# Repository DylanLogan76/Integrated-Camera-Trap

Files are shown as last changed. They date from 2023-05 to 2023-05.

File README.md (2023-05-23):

Integrated-Camera-Trap

Advisors: <br />
Professor Duncan Irschick: (https://www.bio.umass.edu/biology/about/directories/faculty/duncan-j-irschick) <br />
Professor David Schmidt: (https://mie.umass.edu/faculty/david-schmidt) <br />
Professor Marco Duarte (ECE SDP Advisor) : (https://ece.umass.edu/faculty/marco-duarte) <br />

Network of Raspberry Pis connected with Camera Modules to take synchronized pictures via WIFI using Message Query Telemetry Transport (MQTT) (Mosquitto) triggered by motion sensors

If you need access to this repository, contact me at my email address: dylanlogan76@gmail.com and cc Professor Duncan 
Irschick and/or Professor David Schmidt and ask them to grant permission. Please provide your github username as well.

Past work by:
Senior Design Project 2020 Team 15

Members: <br />
Anamitra Datta  <br />
Max Haimowitz <br />
Xiaoyang Pan <br />
Minting Chen <br />

Indepedant Study: Zalman Lipschitz
                  Dylan Logan

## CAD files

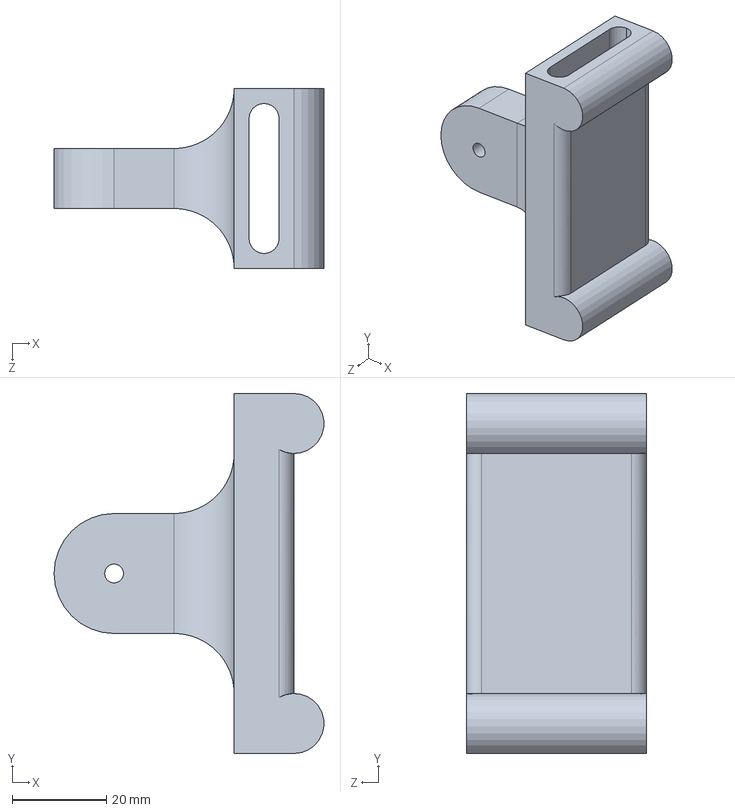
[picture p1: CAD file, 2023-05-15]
Enclosure_Files/Mount.SLDPRT
57.1 x 76.2 x 38.1 mm

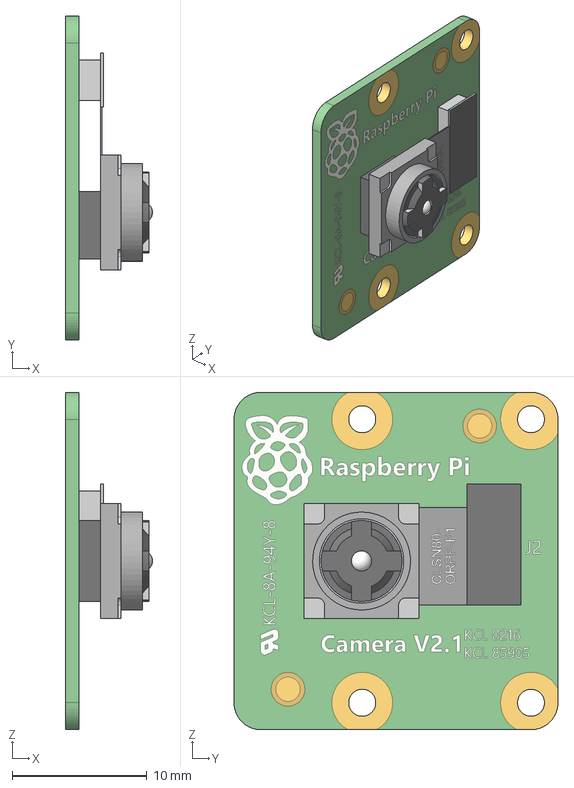
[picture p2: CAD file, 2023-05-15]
Enclosure_Files/Cam V2.1 v1.step
6.45 x 24.0 x 25.0 mm

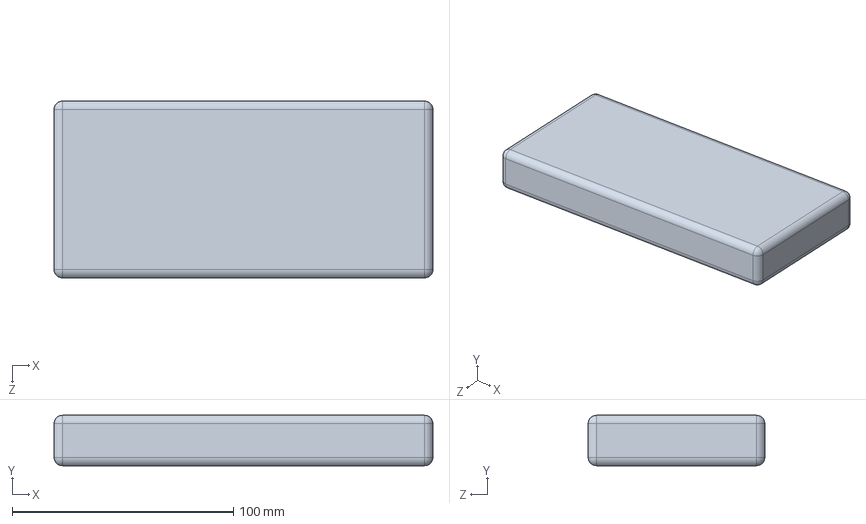
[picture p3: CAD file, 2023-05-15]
Enclosure_Files/Battery Mockup.SLDPRT
171.4 x 22.9 x 80.0 mm

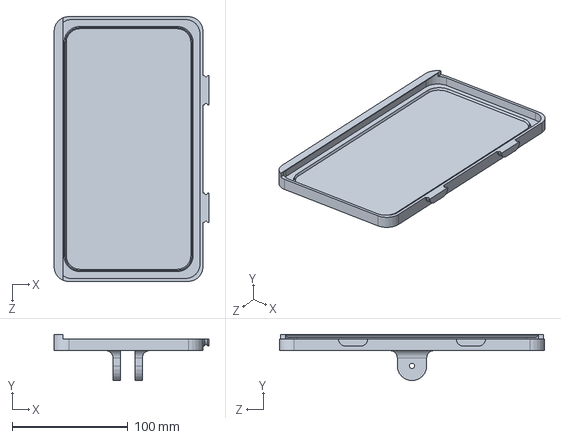
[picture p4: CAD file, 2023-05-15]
Enclosure_Files/Lid.SLDPRT
133.6 x 39.9 x 228.6 mm

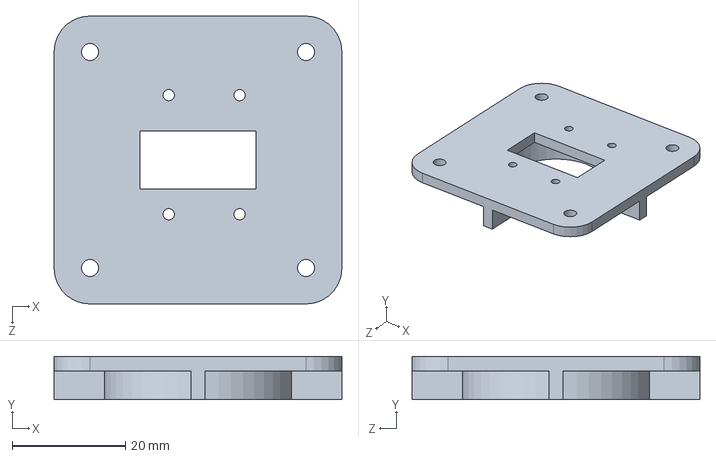
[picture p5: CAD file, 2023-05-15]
Enclosure_Files/Camera Bracket.SLDPRT
50.8 x 7.62 x 50.8 mm

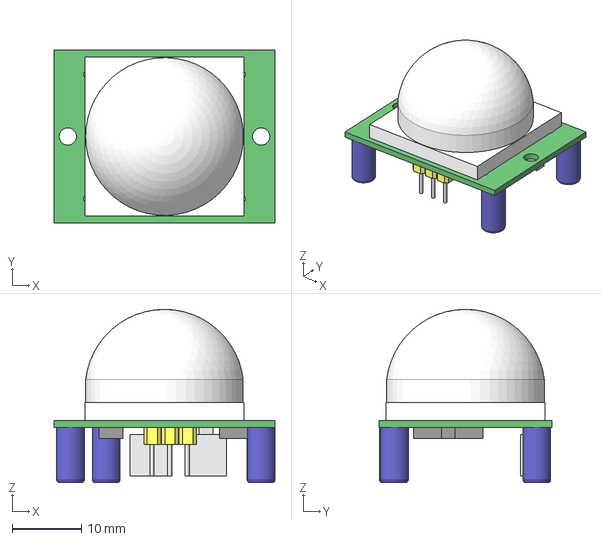
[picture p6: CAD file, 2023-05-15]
Enclosure_Files/HCSR501.step
32.0 x 25.0 x 25.1 mm

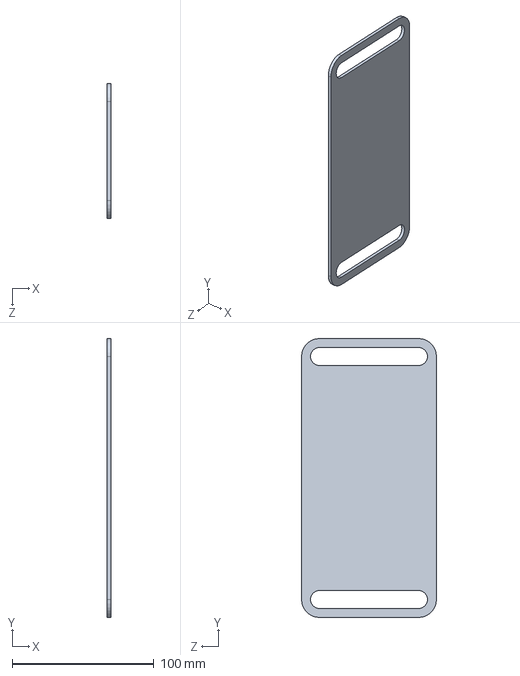
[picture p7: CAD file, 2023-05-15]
Enclosure_Files/Separator.SLDPRT
2.54 x 196.9 x 95.2 mm

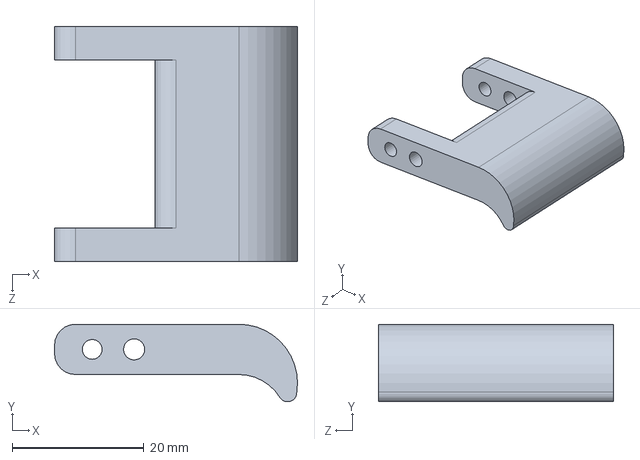
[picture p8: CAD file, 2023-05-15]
Enclosure_Files/Latch.SLDPRT
36.8 x 11.7 x 35.6 mm

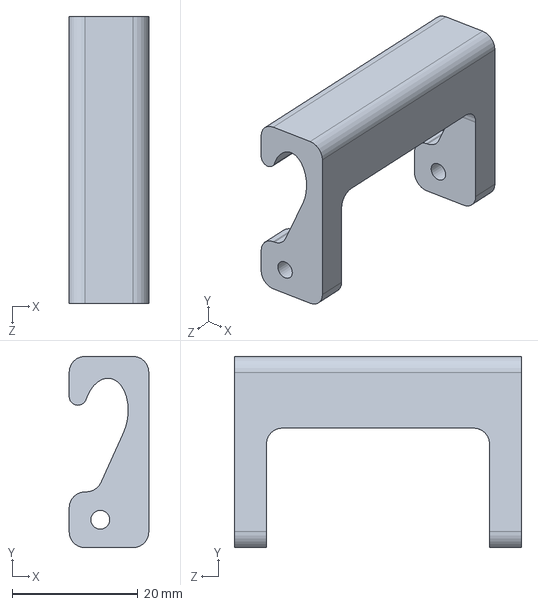
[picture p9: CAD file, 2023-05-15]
Enclosure_Files/Hook.SLDPRT
12.7 x 30.5 x 45.7 mm

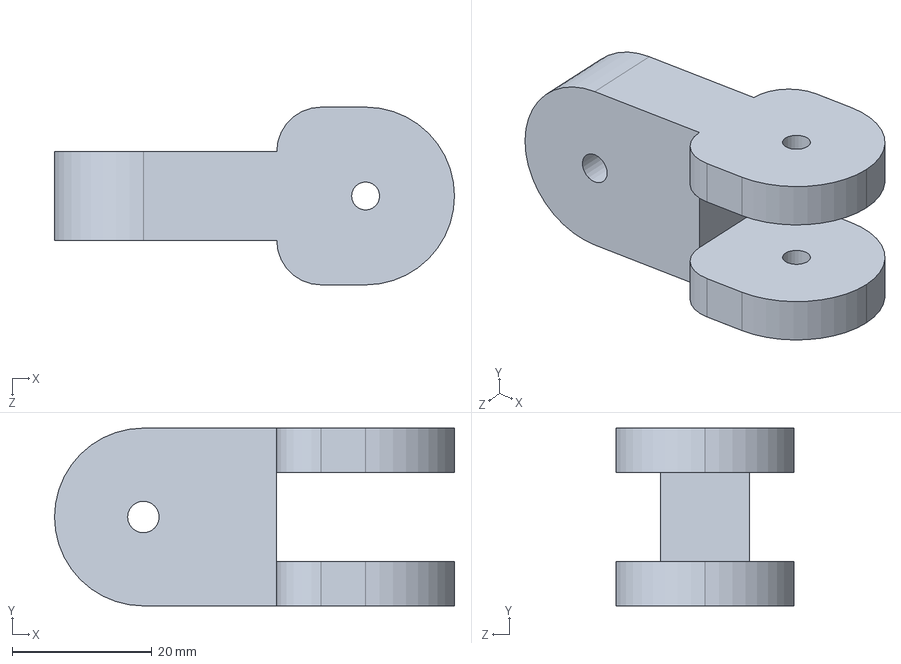
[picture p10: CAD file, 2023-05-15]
Enclosure_Files/Swivel.SLDPRT
57.2 x 25.4 x 25.4 mm

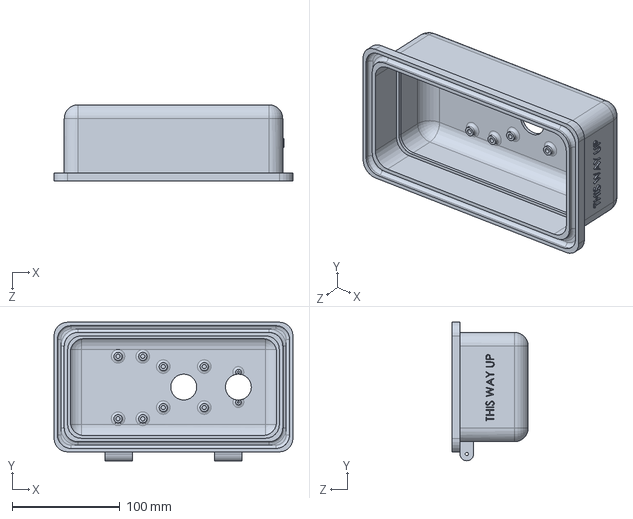
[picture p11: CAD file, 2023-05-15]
Enclosure_Files/Case.SLDPRT
222.2 x 128.9 x 71.1 mm

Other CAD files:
Enclosure_Files/Hook_Legacy.SLDPRT

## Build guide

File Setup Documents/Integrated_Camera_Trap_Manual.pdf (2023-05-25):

# Integrated Camera Trap

## Installation Guide and Instruction Manual

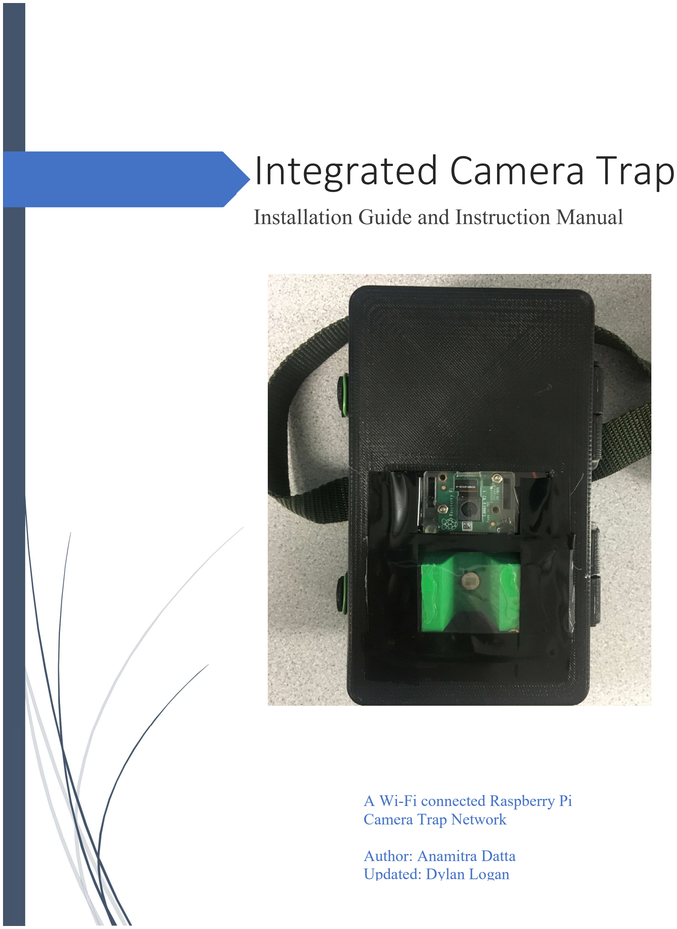
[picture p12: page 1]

A Wi-Fi connected Raspberry Pi Camera Trap Network

Author: Anamitra Datta
Updated: Dylan Logan

1

## Contents

2

3

## 1. Introduction

### a. Background

Camera Traps have been used by biologists and wildlife researchers to observe animals through the use of photos and 3D modeling rather than dangerous and disruptive physical techniques such as tranquilization and traps which can disturb and harm animals. However, the problem with current camera traps is that they are neither connected nor synchronized. This becomes an issue when photo sets generated by the camera traps are used for 3D modeling, resulting in poor, disconnected, and fragmented models as a result of desynchronized photos. Our system aims to improve this issue by connecting the camera traps through Wi-Fi and ensuring photo capturing synchronization through timed messages sent over Wi-Fi, telling each camera trap when to take a photo.

### b. Network Design

Our network uses a master-slave paradigm in which one “master”/main device sends messages to all the of the “slave”/secondary devices when to take a photo. The figure below shows how to the system is set up.

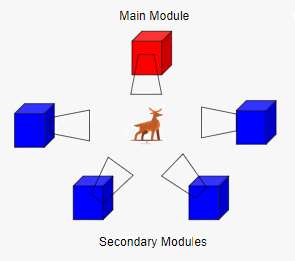
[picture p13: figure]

The camera traps should be arranged in a circle around a single point/area of focus where an animal is likely to appear. There should only be one “master” device in the network and the rest of the devices should be “slave” devices.

4

### c. Hardware

Our camera trap runs on a Raspberry Pi Zero WH (Wireless with Headers) as shown below

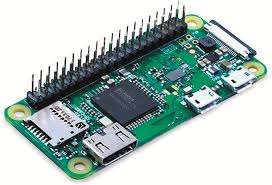
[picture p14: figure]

A Raspberry Pi is a small single-board computer. This board functions like a normal computer in which you can run software and even install physical components.
More information about the Raspberry Pi can be found on the official Raspberry Pi website: https://www.raspberrypi.org/

### d. Software and Networking

The system runs on Wi-Fi through the use of either a router or a wireless access point that can be set up using a Raspberry Pi.
The messages sent within the system are through the use of MQTT (Message Queuing Telemetry Transport). A “broker” is used to send or “publish” messages to all devices listening or “subscribing” to an MQTT “topic” or channel within a network. The broker/publisher and subscribers can be set up using Mosquitto, a free, open-source software for MQTT. More information about Mosquitto can be found on the official Mosquitto website: https://mosquitto.org/
The code running the camera synchronization and photo capturing script is written in Python. More information about Python can be found on the official Python website: https://www.python.org/

5

## 2. Unix

### a. Introduction to Unix

The Raspbian OS that the Raspberry Pi uses is part of the Linux/Unix OS family. Knowledge of this OS and how to use it is necessary for this system. This chapter covers all of the basic topics of the Raspbian OS that are needed for this system to function.

### b. Basic commands

The main way people use a Linux/Unix based operating system is through the command line or terminal. In this section we will cover some basic command line functions so you can get used to working in a Linux/Unix environment. Documentation for Linux commands: http://man7.org/linux/man-pages/index.html . Also type “man <command name>” to get information about a particular Linux command.
i. ls
This lists the contents of the directory you are currently in or the directory you specify
ii. cd
This changes the directory you are currently in. If you want to change to a different directory type this command.
iii. mv
Move a file to a destination directory optionally with a different name and delete the old file. iv. cp
Copy a file to a destination directory optionally with a different name and preserve the old file.
v. rm
Remove a file or directory
vi. mkdir
Make a directory
vii. pwd
Print the current working directory you are in.

6

Permissions
Permissions control who can read, write, or execute a file or directory. Root has the highest permission in Unix subsystems. To be a root user, you must in the sudoers list in the operating system (you are automatically in it by default on Raspbian). Next you must type in the command “sudo su” to change to the root user. Sometimes you need a password to become the root user. If you ever need root privilege to execute a command type “sudo” before your whole command. viii. chmod
Change read, write, and execute permissions of a file.
ix. chown
Change who owns a file or directory.

### c. Processes

Programs and other software that run on an Operating System are referred to as processes. When you execute a program or command, it will run as a process. Here are commands that deal with processes:
i. ps
Lets you view all process running on the operating system. Alternatives include top or htop ii. kill
Kill or stop a process from executing

### d. Power

i. reboot
Restart/reboot the Pi
ii. poweroff
Shutdown the Pi.

### e. Startup services

In our system, we have programs that must start up immediately when the Raspberry Pi boots up. There are many different ways to start programs up on boot.

i. rc.local
This is a file that starts just after all normal services have been started. This is just a bash script file which can run shell commands or any software commands. It is located in the /etc/ folder.

For example, we can start the mobile app with the command “python -u ct_mobile_server.py > output.txt 2>error.txt </dev/null &” and put it in the rc.local file. This starts the mobile app

7

server as a background process and writes the output and errors to separate files on startup, as long as it connected to a proper Wi-Fi network.

ii. Systemd
https://www.freedesktop.org/wiki/Software/systemd/https://www.raspberrypi-spy.co.uk/2015/10/how-to-autorun-a-python-script-on-boot-using-systemd/
Systemd is a service manager which can control which process can run on startup and run them as a service file.

To set a python program (for example, the CT slave program) as a systemd service, write the service file with the command “sudo nano /lib/systemd/ctslave.service”
(Note: these can also be saved to the /lib/systemd/services directory)

Add in the following to the ctslave.service file and save it:
[Unit]
Description=Camera Trap Slave Service After=network-online.target Wants=network-online.target

[Service]
Type=idle
User=pi
ExecStart=python -u /home/pi/ct_client_slave.py

[Install]
WantedBy=network-online.target

Give the file root permissions with the command “sudo chmod 777 /lib/systemd/ctslave.service” Type in the commands “sudo systemctl daemon-reload” and “sudo systemctl enable ctslave.service” and then reboot the pi. The program should successfully run on startup. You can check using “sudo systemctl status ctslave.service” . You can check the output of the service using journalctl.

You can start the mobile app server or the slave or master CT programs using systemd

iii. Cron
http://man7.org/linux/man-pages/man5/crontab.5.html
Cron is a software utility which provides a time based job scheduler. You can start scripts or programs at specific times. Here is a guide on how to write a crontab to automatically start a program or command: https://help.ubuntu.com/community/CronHowto

8

## 3. Installation and Setup

### Camera Trap Raspberry Pi a. Supplies

The supplies we used are listed below, but you can use any components that are similar and fit within the enclosure
PIR Motion Sensor | Adafruit | HC-SR501 | $10.00
Raspberry Pi Zero WH | Raspberry Pi | Zero WH | $14.00
Raspberry Pi Camera Module V2 (8 Megapixel,1080p) | Raspberry Pi | V2, 8MP, 1080p | ~$25.00

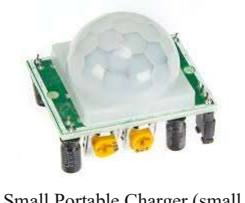
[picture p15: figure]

Portable Charger | Sethruki | 20000mAh, T-28 | ~$25.00
Raspberry Pi Zero WH (Wireless With Headers) | HC-SR501 PIR Motion Sensor

Small Portable Charger (small

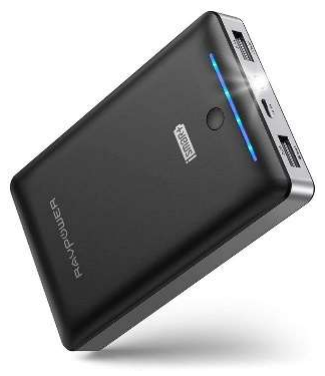
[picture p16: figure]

enough to fit in enclosure)

MicroSD card (16-32 GB) and SD Card Adapter | Micro USB to USB adapter or
| USB Hub (for USB Wireless Mouse and Keyboard)

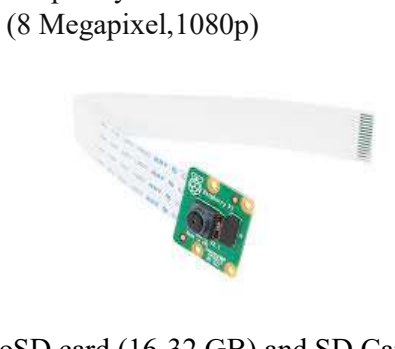
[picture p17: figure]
(8 Megapixel,1080p)

Raspberry Pi Camera Module V2

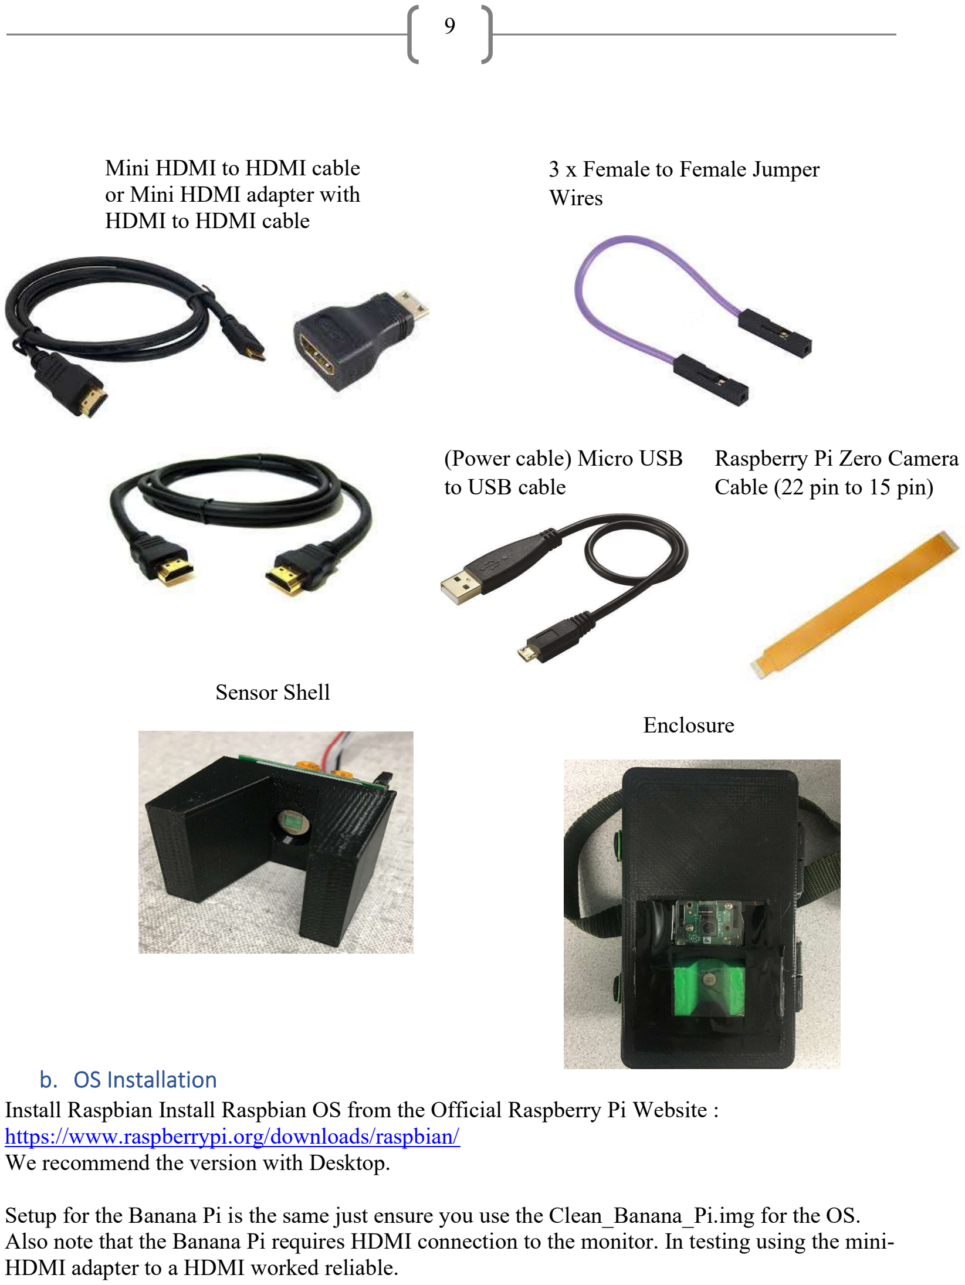
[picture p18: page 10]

9

### b. OS Installation

Install Raspbian Install Raspbian OS from the Official Raspberry Pi Website : https://www.raspberrypi.org/downloads/raspbian/
We recommend the version with Desktop.

Setup for the Banana Pi is the same just ensure you use the Clean_Banana_Pi.img for the OS. Also note that the Banana Pi requires HDMI connection to the monitor. In testing using the mini-HDMI adapter to a HDMI worked reliable.

Mini HDMI to HDMI cable
or Mini HDMI adapter with
HDMI to HDMI cable

### 3 x Female to Female Jumper

Wires

(Power cable) Micro USB
to USB cable

Raspberry Pi Zero Camera
Cable (22 pin to 15 pin)

Sensor Shell
Enclosure

10

Put the microSD card in the SD Card adapter and put the SD card adapter into your SD card slot on your computer.
First, unzip the downloaded folder to get an .img file of the Operating system you want to install on the Pi. To install the Raspbian OS on the microSD card, we recommend to use Etcher : https://www.balena.io/etcher/ . Flash the image or .img file onto the SD card and remove the microSD card from the SC card adapter when the installation is complete.

### c. Setting up the Raspberry Pi

i. Add components and start up OS

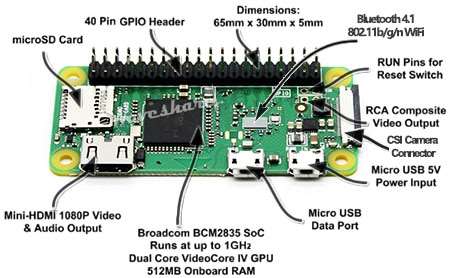
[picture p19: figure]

Place the microSD card into the microSD card slot on the Raspberry Pi

Put the 22 pin side of the wire on the bottom slot of the camera module and the 15 pin side of the wire in the Raspberry Pi CSI camera connector on the end of the Pi. Make sure the dark or white part of the wire faces up. Make sure the camera is attached as shown below.

11

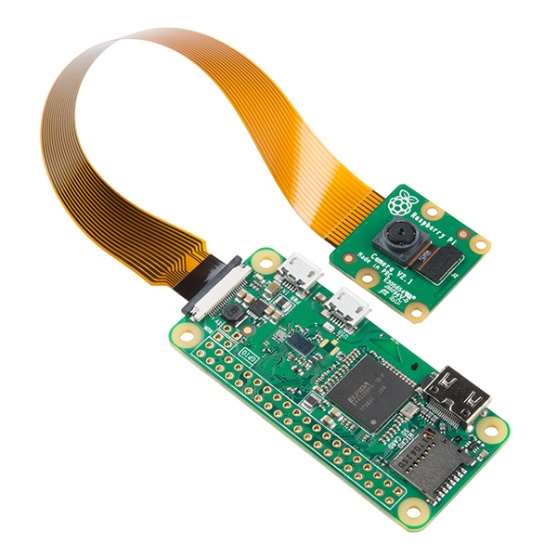
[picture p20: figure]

Attach the PIR Sensor with the female to female jumper wire cables to the Raspberry Pi Zero as shown below. Make sure the pins match with each other.

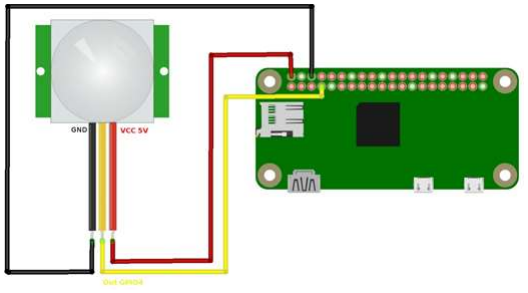
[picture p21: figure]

Plug in the Micro USB to USB adapter/hub in the Micro USB data port and attach your wireless USB Mouse and Keyboard
Plug in the mini HDMI to HDMI cable or mini HDMI adapter to the mini HDMI port and attach an HDMI cable to a computer Desktop monitor
Finally, plug in the power cable to the Pi in the micro USB power input port and attach it to a power outlet or a small portable charger
A few Raspberry Pi logos, a rainbow-colored screen, and maybe some startup scripts should appear. This means that the Raspbian OS is booting up and you had successfully installed the OS on the Pi. If it does not work, make sure you have followed all of the steps, make sure the Pi works properly and make sure the image is installed on the microSD card correctly and make sure the microSD card is working properly.

12

The default username is "pi" and the default password is "raspberry"
The default username is “pi” and the default password is “bananapi”

You can change the password for user "pi" if you want, but it is not necessary. Follow these instructions: https://www.raspberrypi.org/documentation/linux/usage/users.md

If you want to change the password, use the command “passwd” or type in “sudo raspi-config” and select option 1. Change User Password

If you are using a Headless Raspbian OS without a GUI/Desktop, edit XKBLAYOUT line in /etc/default/keyboard from "gb" to "us" using nano with the command “sudo nano /etc/default/keyboard”

ii. Wi-Fi Setup
Follow these instructions to set up Wi-Fi depending on your setup: https://www.raspberrypi.org/documentation/configuration/wireless/ You need to connect to the Internet for the next few steps.
Desktop:
In the upper right corner, there should be network icon that looks like this:
Click it, and click on the Wi-Fi network you want to connect to and type in the password of the Wi-Fi network. When the icon becomes fully blue, you should be fully connected to Wi-Fi Command Line:
Type in “sudo raspi-config” and select 2. Network Options and then 2.Wi-Fi. Type in the ssid of the network you want to connect to and its password. After that, reboot the Pi and you should be connected to the Wi-Fi network you specified.
Or
You can edit the /etc/wpa_supplicant/wpa_supplicant.conf file to add this line at the bottom: network={
| ssid="<name of Wifi Network>" psk="<Password for that Wifi Network>"

}

Then reboot the Pi and should you be able to connect to the Wi-Fi network specified. Depending on your Wi-Fi network configurations, you might need to add extra parameters to connect, see the documentation for more details,
http://w1.fi/cgit/hostap/plain/wpa_supplicant/wpa_supplicant.conf -Documentation for wpa_supplicant.conf

13

To set up a static IP address for the Raspberry Pi, edit the dhcpcd.conf file using the command “sudo nano /etc/dhcpcd.conf” and add the following line with the ip address you want to set the Pi to specifically (24 is the subnet mask)
static ip_address=192.168.5.1/24

iii. Installation software and enabling interfaces
When you are connected to the internet, type in the following in the command line and type "y" when asked to install the following:
sudo apt-get update
sudo apt-get upgrade
sudo apt-get install mosquitto mosquitto-clients sudo apt-get install python-pip
sudo pip install paho-mqtt
sudo apt-get install ftpd
sudo pip install gpiozero
sudo pip install picamera
sudo apt-get install fbi
sudo apt-get install sshpass
sudo apt-get install python-paramiko

SSH (protocol to log into Pi remotely) is disabled by default, we need to enable SSH to enable SSH:

### 1. type "sudo raspi-config" in the command line 2. Select 5.Interfacing Options 3. Select P2 SSH 4. reboot the pi by typing "sudo reboot" in the command line

SSH in now enabled and you can SSH into the Pi from any device using a software client or through command line (https://man.openbsd.org/ssh)

FTP or SCP files from https://github.com/anamitradatta/Integrated-Camera-Trap for each Pi. We recommend an FTP or SCP client:

WinSCP (Windows only)
Filezilla
Cyberduck

The camera is disabled by default, we need to enable Camera

14

to enable camera:

### 1. type "sudo raspi-config" in the command line 2. Select 5.Interfacing Options 3. Select P1 Camera 4. reboot the pi by typing "sudo reboot" in the command line

The Camera is now enabled and working
If you want to test the camera, run test_camera.py to see if it can take a photo "test_photo.jpg"

In the main source code folder, type in the command "sudo chmod 777 ./*" and "sudo chown pi ./*" to run all files as user pi without root permissions

Make a directory called cameraTrapPhotos in the /home/pi directory.

Python should be pre-installed on Raspbian OS. Make sure python or python3 is installed on your OS by typing in "python --version", if returns nothing, then you need to install python for Linux https://www.python.org/downloads/source/

### Access Point Raspberry Pi

In our system, we will be using and setting up a Raspberry Pi Zero W to act as an access point or router in our system so we do not need the use of a physical router or switch in our network.
i. Supplies
Raspberry Pi Zero W or WH | Small Portable Charger (small enough to fit in enclosure)

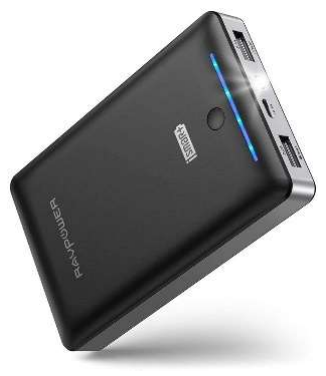
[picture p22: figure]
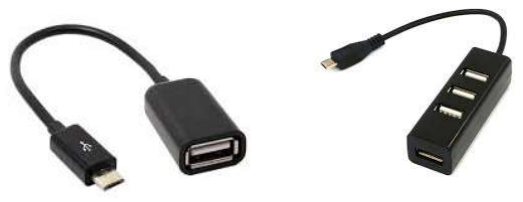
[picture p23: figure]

Micro USB to USB adapter or USB Hub (for USB Wireless
Mouse and Keyboard)

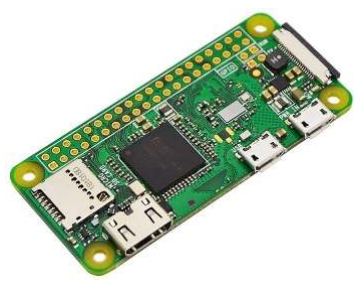
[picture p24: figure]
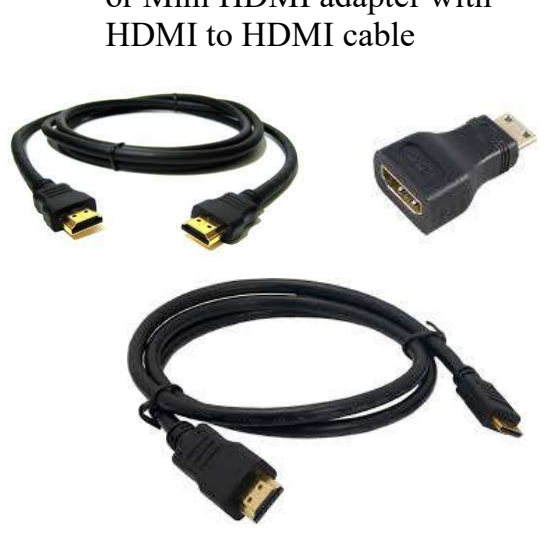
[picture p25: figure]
HDMI to HDMI cable

Mini HDMI to HDMI cable
or Mini HDMI adapter with

15

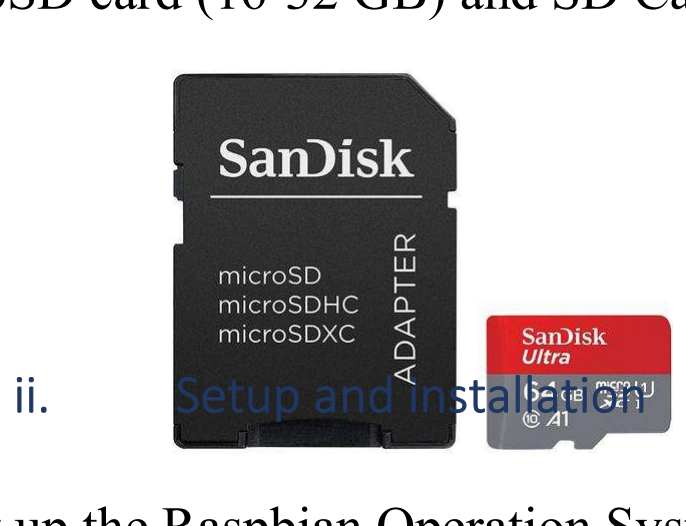
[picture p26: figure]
Setup and installation

Set up the Raspbian Operation System with Desktop as you did before for the camera trap Raspberry Pi and connect to the Internet.

We will now set up the Raspberry Pi as an access point (AP).

Here is a guide to setting up the Pi as an access point, which we will cover in this section: https://learn.sparkfun.com/tutorials/setting-up-a-raspberry-pi-3-as-an-access-point/all
All files are also available on the Github if needed for reference under the AP_Files folder. We will need to use nano (an inbuilt text editor) to change some configuration files. To save a file in nano, press ctrl + o and then ctrl + x to exit the file. Nano documentation: https://www.nano-editor.org/docs.php
When you are connected to the internet, type in the following in the command line and type "y" when asked to install the following:
sudo apt-get update
sudo apt-get upgrade
sudo apt-get install ftpd
sudo apt-get install hostapd
sudo apt-get install dnsmasq

First make a backup of all files we will be editing with the commands: sudo cp /etc/dhcpcd.conf /etc/dhcpcd.conf.backup
sudo cp /etc/network/interfaces /etc/network/interfaces.backup
sudo cp /etc/hostapd/hostapd.conf /etc/hostapd/hostapd.conf.backup
sudo cp /etc/dnsmasq.conf /etc/dnsmasq.conf.backup

We are going to set a static IP address on our AP Raspberry Pi. Edit the dhcpcd.conf file with the command “sudo nano /etc/dhcpcd.conf”. Go to the bottom of the file and add the following line and save the file:
denyinterfaces wlan0

Next, edit the interfaces file with the command “sudo nano /etc/network/interfaces”
Go to the bottom of the file and add the following and save the file:

MicroSD card (16-32 GB) and SD Card Adapter

16

auto lo
iface lo inet loopback

auto eth0
iface eth0 inet dhcp

allow-hotplug wlan0
iface wlan0 inet static
address 192.168.5.1
netmask 255.255.255.0
network 192.168.5.0
broadcast 192.168.5.255
Next we have to configure hostapd, which allows the Raspberry Pi’s WiFi chip to broadcast an SSID and allow Wi-Fi connections on a certain channel
Edit the hostapd.conf file with the command “sudo nano /etc/hostapd/hostapd.conf”

Enter the following into the file and save the file:
interface=wlan0
ssid=CTWifi
hw_mode=g
channel=7
ieee80211n=1
wmm_enabled=1
ht_capab=[HT40][SHORT-GI-20][DSSS_CCK-40] macaddr_acl=0
auth_algs=1
ignore_broadcast_ssid=0
wpa=2
wpa_key_mgmt=WPA-PSK
wpa_passphrase=cameratrap
rsn_pairwise=CCMP
wpa_pairwise=TKIP

Feel free to change the ssid and wpa_passphrase to whatever you like. These are your Wi-Fi name and the Wi-Fi password. In our example, we use CTWifi as the SSID and cameratrap as the password for the CTWifi network.

Edit the hostapd startup script with the command “sudo nano /etc/default/hostapd”

Find the line where it says #DAEMON_CONF=”” and replace it with: DAEMON_CONF=”/etc/hostapd/hostapd.conf”

Next we have to set up the DHCP server which hands out IP addresses to different devices connected to the network.

Edit the dnsmasq.conf file with the command “sudo nano /etc/dnsmasq.conf”

17

Add the following to the bottom of the file and save it: interface=wlan0
listen-address=192.168.5.1
bind-interfaces
server=8.8.8.8
domain-needed
bogus-priv
dhcp-range=192.168.5.100,192.168.5.200,24h

You can also assign static IPs to specific devices in dnsmasq.conf, for example if the device with MAC address 00:00:5e:00:53:42 was designated as the slave#2, we could set up a static IP for that device by adding the following line to the dnsmasq.conf file:

dhcp-host=00:00:5e:00:53:42,ctslave2,192.168.5.102

This will have the DNS server assign a name to this device and give a static IP of 192.168.5.102 as well. You can optionally do this for the devices, so you can refer the device as a name rather than an IP address.

You can edit the dhcp range from anything from 192.168.5.2 to 192.168.5.254. But remember, the AP Pi uses 192.168.5.1, so do not assign a Pi with that IP address.
Now reboot your Pi. You can test if the Wi-Fi access point works from your computer. You can connect to it by typing in the password you have in the hostapd.conf file.

You have now successfully built the Access Point Pi for the camera trap network.

You can connect the other Pis to the AP network by either using the WiFi icon/raspi-config and inputting the password or editing the wpa_supplicant.conf file with the ssid and password you chose for the AP.

### d. How to run the code

In the main source code folder, type in the command "sudo chmod 777 ./*" and "sudo chown pi ./*" to run all files as user pi without root permissions. Make a directory called cameraTrapPhotos in the /home/pi directory

Python should be pre-installed on Raspbian OS. Make sure python or python3 is installed on your OS by typing in "python --version", if returns nothing, then you need to install python for Linux https://www.python.org/downloads/source/. Make whatever changes to parameters are needed in the code. Type "python <name of python file>" to run the code

You must turn on the master Pi before the slave Pis and make sure they are all running on the same network. Run the slave Pis first with the command “python ct_client_slave.py”, and then when all the slave Pis are running, run the Master code with the command “python ct_master_multi.py”. (Note: the updated slave code is called ct_slave_23.py or dylan_slave.py if it has not been renamed on the pi)

18

Either run the single sensor photo triggering or the multiple sensor photo triggering. Do not run both at the same time. (Note: the multisensory version should be used for more reliability)

There should only be one master running and multiple slaves running. Make sure the slave Pi programs have the IP address of the master Pi in their code and are connected to the network.

In this section, we will show how to run the single sensor camera trap program.

First run the slave Pis. Be sure the master Pi is on and has the software installed. The message below should appear on the slave Pis if everything is set correctly.

When all the slave devices are on and connected, run the master pi. This message should appear.

After a few seconds, the master Pi will wait for the motion sensor to be triggered. When the motion sensor senses something, it will start the photo session.

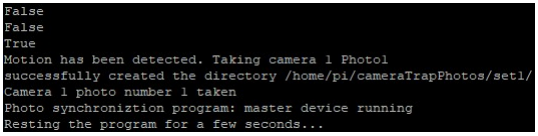
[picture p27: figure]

The slave device will receive a message when motion has been detected from the master Pi and will also take a photo and send it to the master device as shown in the screenshot below. Here we only have one slave device running.

19

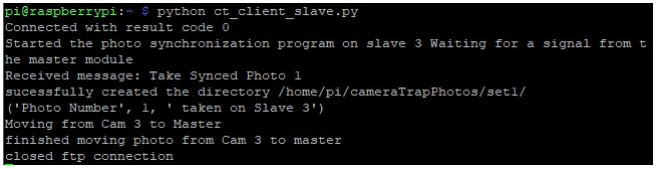
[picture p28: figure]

On the master Pi, in the cameraTrapPhotos directory, you should have some photo sets with photos from all cameras running as shown below

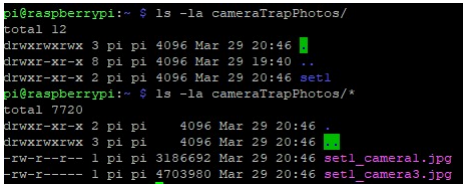
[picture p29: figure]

The multiple sensor camera trap program runs the same way.

First, make sure the master device is on and run the slave Pis and the message below should appear if everything is set correctly.

Then run the master Pi when all the slave devices have started running. The command to run the master code is: python ct_master_multi.py The message below should appear

After a few minutes, the master device should get a response from all slave devices as shown below. Here we only have one slave device running.

20

Then the master device will get the sensor readings from all slave devices. If the percentage of “true” sensor readings from all sensor devices is greater than some threshold (in this example, we used 67%), it will trigger a photo, else it will not and will rest and repeat the process.

When the master starts a photo session, it will send a message to the slave devices to take a photo and send it to the master device.

21

### e. Setting up mobile app

To set up the mobile app, we first need to install Android Studio: https://developer.android.com/studio

Download the mobile app folder from Github

In Android Studio, go to the “File” tab, and select “import project”. Select the mobile app folder you downloaded.

Plug in your Android phone via USB into your computer. To download the app onto your phone, you must go into your phone’s settings and enable USB debugging.

Run the app by clicking on the run button or go to the “Run” tab and click “Run App”
The app should be installed on your phone

On your phone, you must also install an FTP server app, we recommend this app: https://play.google.com/store/apps/details?id=com.medhaapps.wififtpserver&hl=en_US

Make sure that the port number is 2221 and the username and password are set to the ones in the code. The default using our recommended app is username:android, password:android . Start the FTP server on. Make sure the settings are similar to the one shown below

22

### f. Setting up mobile server

Download the ct_mobile_server.py from Github. Make sure the IP address, client port, and the username and password for the FTP server are the same as the one you are running on the phone.

Run the mobile server code on the Master Pi using the command “python3 ct_mobile_server.py”. Make sure you are connected to the same network the master Pi is on. Make sure the host IP in the code is correctly set to the IP address of the Master Pi. This message should appear on the Pi.

Run the FTP server and mobile app on the phone. Type in the IP address of the Master Pi and the port for the mobile server (default port = 8888) as shown below. You should see a connected text on the mobile app on the next page if you successfully set it up.

23

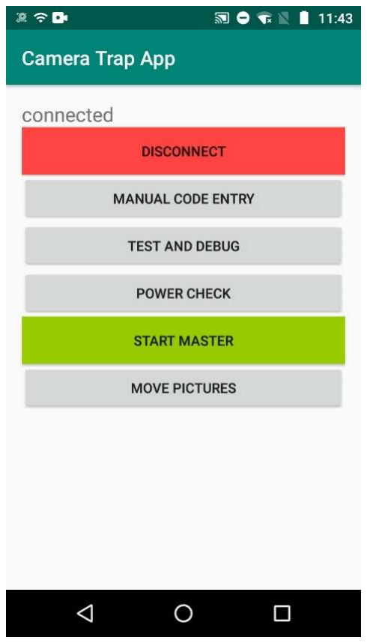
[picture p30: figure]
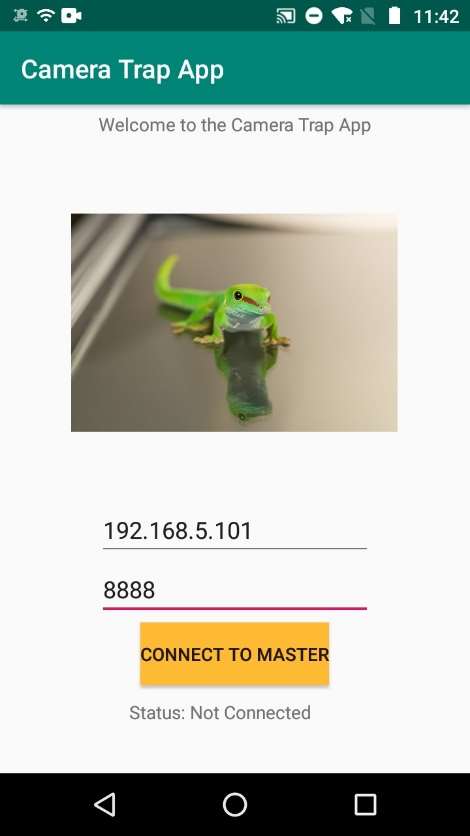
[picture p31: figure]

The phone should be connected now and a message will appear on the master Pi as shown below if successful. From there, as long as the mobile server is running on the master Pi, you can do many options, including downloading the photos onto an SD on your phone. For this, make sure the FTP server is running on your phone. If you are disconnected from the socket connection and cannot connect to the Pi through the phone, restart both the mobile app and the mobile server on the Pi.

To download the photos from the Master Pi, select the “Move Pictures” box.

It will print a notification of “sending pictures” and “sent all photos” as shown below. To see the photos, go to the Downloads directory and you should see your photo sets as shown below

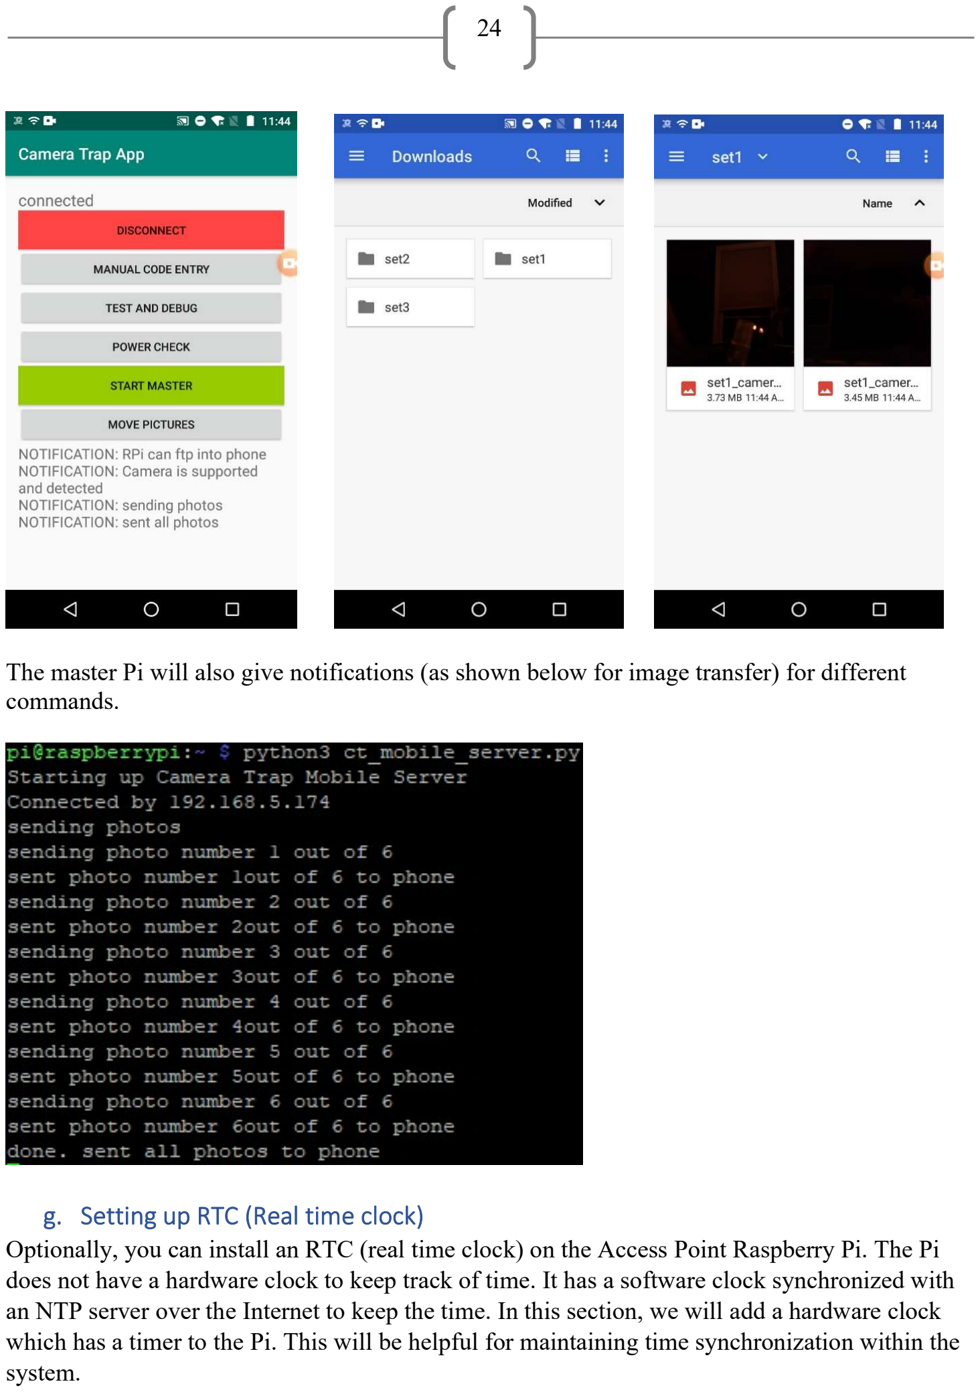
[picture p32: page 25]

24

The master Pi will also give notifications (as shown below for image transfer) for different commands.

### g. Setting up RTC (Real time clock)

Optionally, you can install an RTC (real time clock) on the Access Point Raspberry Pi. The Pi does not have a hardware clock to keep track of time. It has a software clock synchronized with an NTP server over the Internet to keep the time. In this section, we will add a hardware clock which has a timer to the Pi. This will be helpful for maintaining time synchronization within the system.

25

Here is a guide to setting up an RTC on the Raspberry Pi. https://learn.adafruit.com/adding-a-real-time-clock-to-raspberry-pi
Make sure you are connected to the Internet. Set the time of the Pi synced with the NTP server by typing the command “sudo raspi-config”, then select 4. Localisation Options then I2. Change Timezone, and select the time zone you are currently in. This will set the Pi’s time to the time controlled by the NTP server for the time zone you selected.
We recommend using the PCF8523 RTC (https://www.adafruit.com/product/3386), but feel free to use any RTC of your choosing
Put the RTC on the GPIO pins on the end near the SD Card like in the figure below

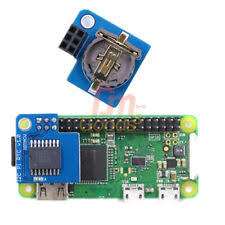
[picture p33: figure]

First ,enable I2C by typing “sudo raspi-config”, then 5. Interfacing Options, then P5. I2C, then reboot the Pi.
Run the command “sudo apt-get install python-smbus i2c-tools”

Then, type “sudo i2cdetect -y 1”. You should see ID # 68 appear, which is the address of the RTC

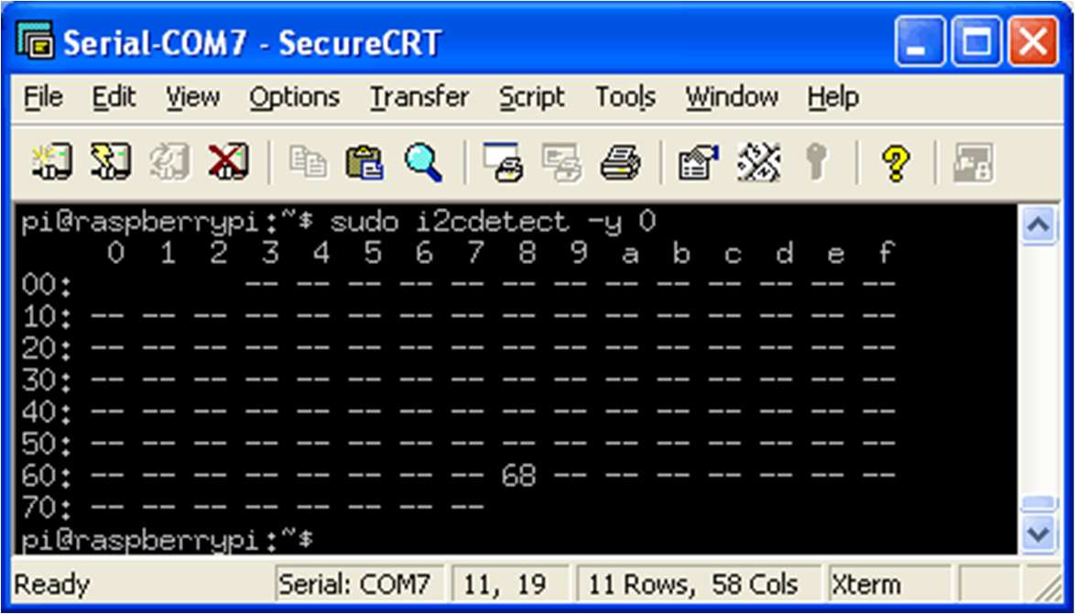
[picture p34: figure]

26

Next, edit the /boot/config.txt file with the command “sudo nano /boot/config.txt”

Add the line:
dtoverlay=i2c-rtc, pcf8523

To the end of the file and save it. Change the RTC name depending on which one you use.

Reboot the Pi and then run “sudo i2cdetect -y 1” again and you should see UU where it showed #68 before

Disable the software clock by running the commands: sudo apt-get -y remove fake-hwclock
sudo update-rc.d -f fake-hwclock remove
sudo systemctl disable fake-hwclock

Now, edit the file /lib/udev/hwclock-set by running the command “sudo nano /lib/udev/hwclock-set”

Comment out these lines by putting a # sign in front of them
if [ -e /run/systemd/system ] ; then
exit 0
fi
Your file should look like this:

27

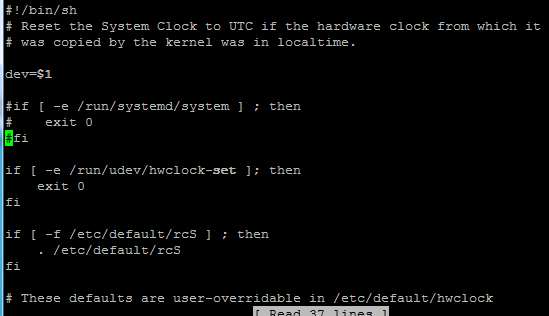
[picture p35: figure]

Also comment out these two lines: /sbin/hwclock --rtc=$dev –systz –badyear /sbin/hwclock –rtc=$dev –systz

Then reboot the Pi again. To read the time from the RTC use the command “sudo hwclock -D -r”. The current time on the hardware clock is invalid. To set the time, first run the command “date” to verify the time is correct. Then run the command “sudo hwclock -w” to write the time to the RTC. Then “sudo hwclock -r” to read the time from the RTC. If the time from the RTC is correctly synced, you have successfully set up the RTC.

You can sync the times of all of the Pis in the network through the Access Point Pi which has the RTC using the timesyncssh.sh file in the AP_Files folder. The access point Pi uses the script’s awk utility to get the IP addresses of all Pis in the network and then ssh individually into each Pi and set the time from its RTC onto each Pi’s time.

28

### h. Setting up the enclosure

### 1. See separate enclosure setup document

## 3. Setup from Image Files

Saved to the github repository are image files from the working Raspberry Pis. These are exact copies of the working modules. In order to utilize these, you must have a micro-SD card the of at least 16 gigabytes and ideally the same brand and model as used here to avoid problems when flashing the image. SanDisk Ultra 16GB was used. This recommendation is here because sometimes problems can arise where different brand cards are slightly different sizes and will then not allow the files to be flashed.
Plug the card into a computer and use an etching tool (balena etcher was used) to copy the correct boot files from the repository. This method is the same as downloading the OS and is detailed above. Connect the PIR sensor and camera and the Pi should be ready for use.
Note under 3.c.ii you set up a static IP address for the Pis. Ensure you don’t set up the Pis with the same static address when copying from the image file or allow the AP Pi to assign IP addresses as they connect.

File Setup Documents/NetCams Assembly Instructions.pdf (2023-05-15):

NetCams

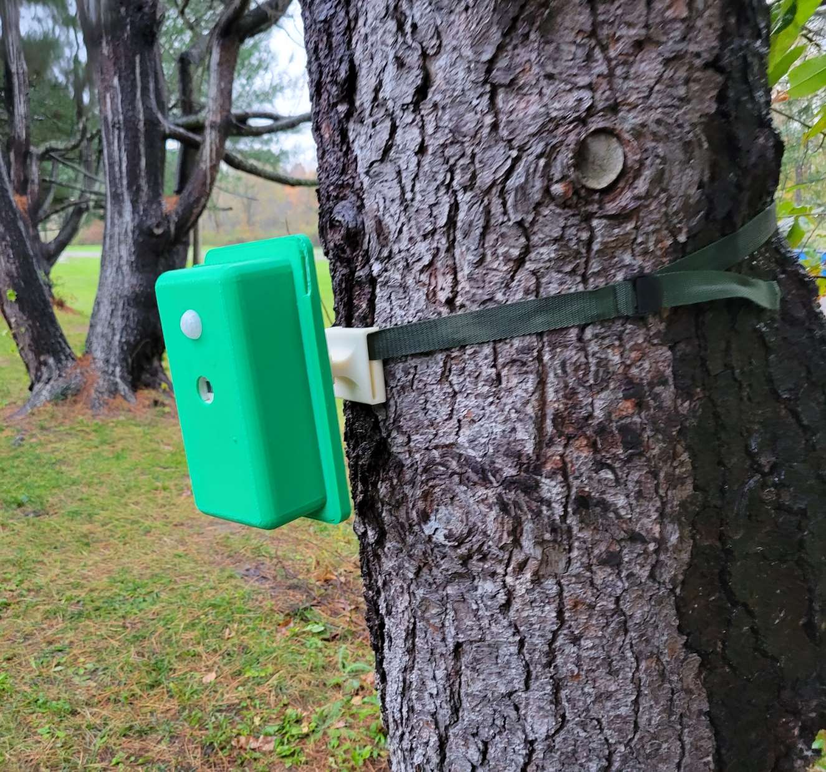
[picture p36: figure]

1

# NetCams Assembly Instructions

2

Index.

### 2. Bill of Materials 4. Labelled pictures of parts 6. Print Instructions and Helpful Tools 7. Assembly Instructions

1

High-Temperature Silicone Rubber Tubing for Air and Water - Soft, Durometer 35A, 1/8" ID, 1/4" OD, Opaque White

2

Heat-Set Inserts for Plastic, Brass, M2.5 x 0.45 mm, 5.9 mm Installed Length

3

18-8 Stainless Steel Hex Head Screw, M4 x 0.7 mm Thread, 30 mm Long

4

18-8 Stainless Steel Wing Nut,M4 x 0.7 mm Thread

5

General Purpose 18-8 Stainless Steel Washer,for M4 Screw Size, 4.300 mm ID, 8 mm OD

6

3M Super Silicone Sealant, Model 8661, 3 oz. Tube

3

7

Black-Oxide Alloy Steel Socket Head Screw, M2.5 x 0.45 mm Thread, 4 mm Long

8

Partially Threaded Steel Stud, M3 x 0.50 mm Thread Size, 10 mm Long

9

Light-Duty Buckles
for 1" Maximum Webbing Width, Sew-on, Plastic Feed Through Part number

10

Zinc-Plated Alloy Steel Socket Head Screw, M2 x 0.4 mm Thread, 5 mm Long

11

Shock-Absorbing Nylon Webbing, 1" Wide, 4 Feet Long, Black

12

HATCHBOX PLA 3D Printer Filament, Dimensional Accuracy +/- 0.03 mm, 1 kg Spool, 1.75 mm, White

Parts.

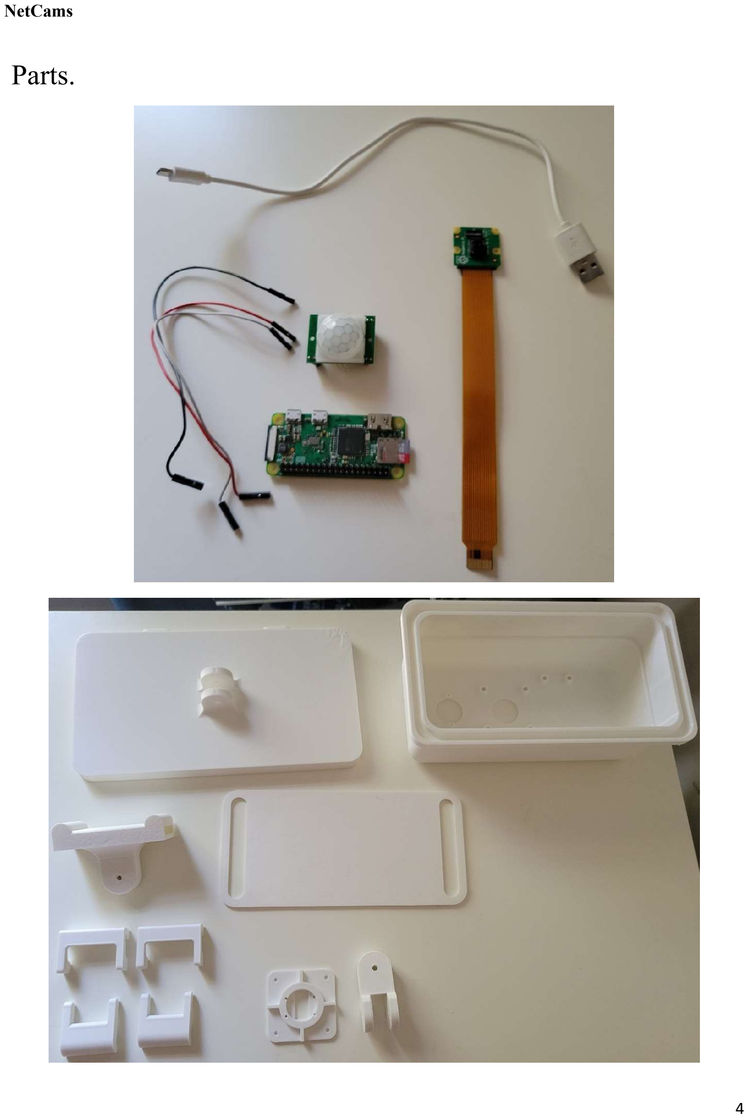
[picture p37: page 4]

4

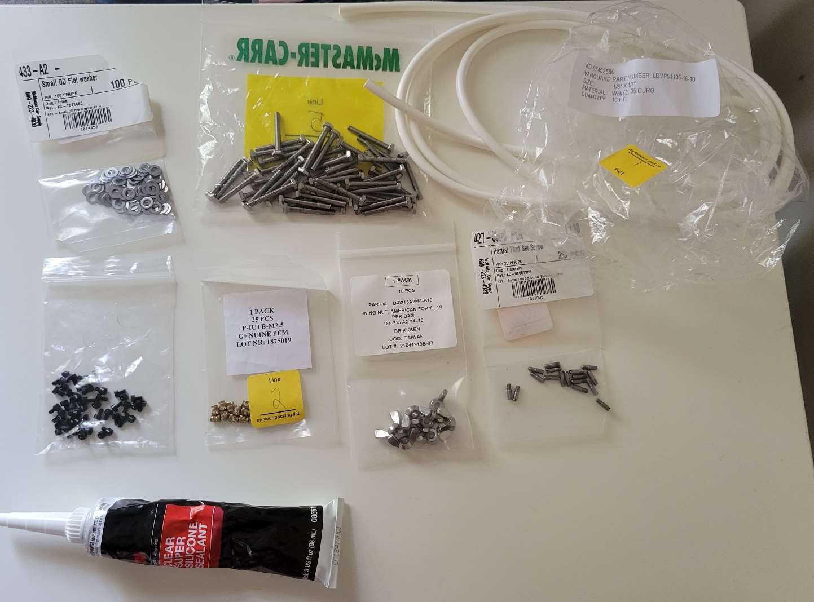
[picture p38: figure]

5

6

Printing.

This is an overview of the minimum print settings to be used. Increasing resolution and infill density is ok but will take longer to print and use more material.
Minimum print area necessary is 9in x 6in x 5in, larger build plate is preferable to prevent warping and to print many parts at once.
There are Cura project files uploaded to the GitHub. To change the printer, go into the project file and choose the correct printer.
By default, the files are sliced for a Creality Ender 3.
All parts can be printed using .3mm layer height and 2 shells.
Lid: The hinge area needs to be 100% infill, so unless variable infill is available (as in Cura), use 100% for the whole part. Otherwise, the rest of the part can be 25% or greater infill.
Camera Bracket: 100%
Latch: 100%
Mount: 100%
Separator: 25%
Swivel: 100%
Case: 25%
Hook: 100%
Helpful Tools.
- 3mm drill bit
- 4mm drill bit
- Soldering iron
- Small flat head screwdriver
- Knife
- Metric allen key set

7

Assembly.

### 1. Use a soldering iron to heat brass inserts (2) into 8 marked holes taking

special care to not push the inserts past being flush with the top surface. 225°C is hot enough to easily insert them.

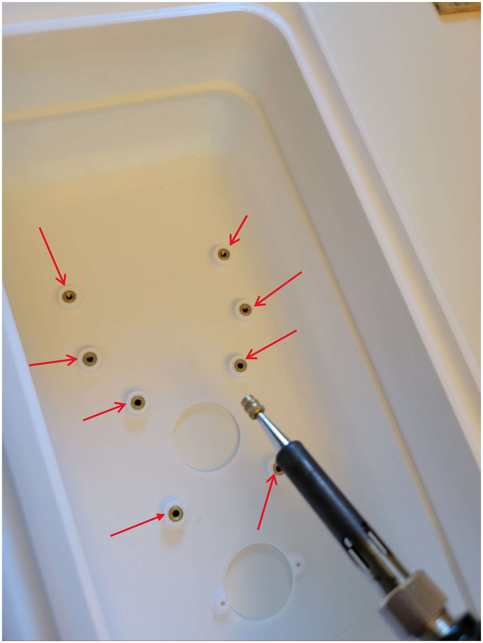
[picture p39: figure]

8

2. Use 4 X Threaded Studs (8) to attach 2 X hinges to the body. If necessary, use a 3mm drill bit to clean up the hole in the

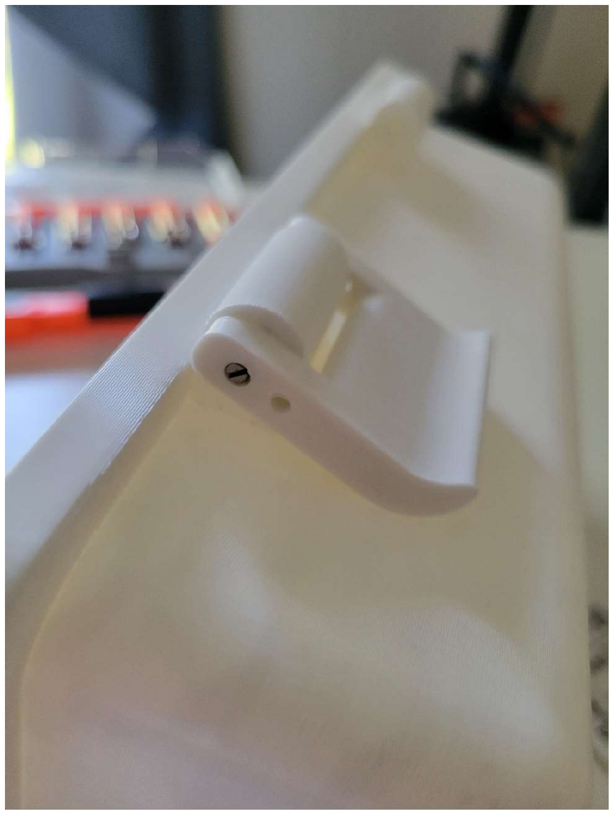
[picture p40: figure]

9

3. Do the same for the latches.

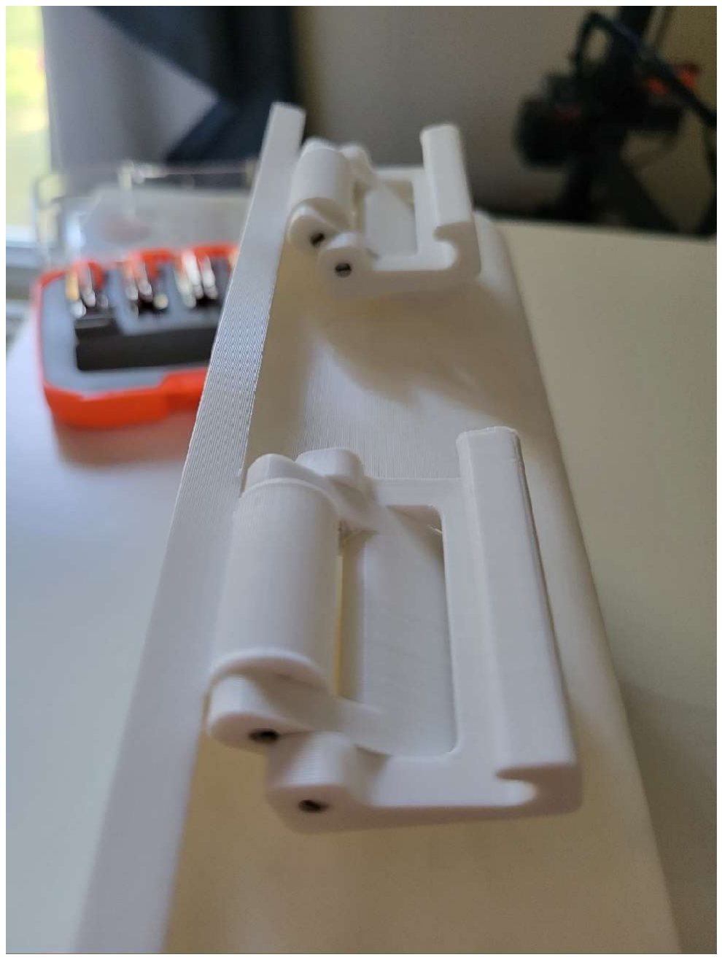
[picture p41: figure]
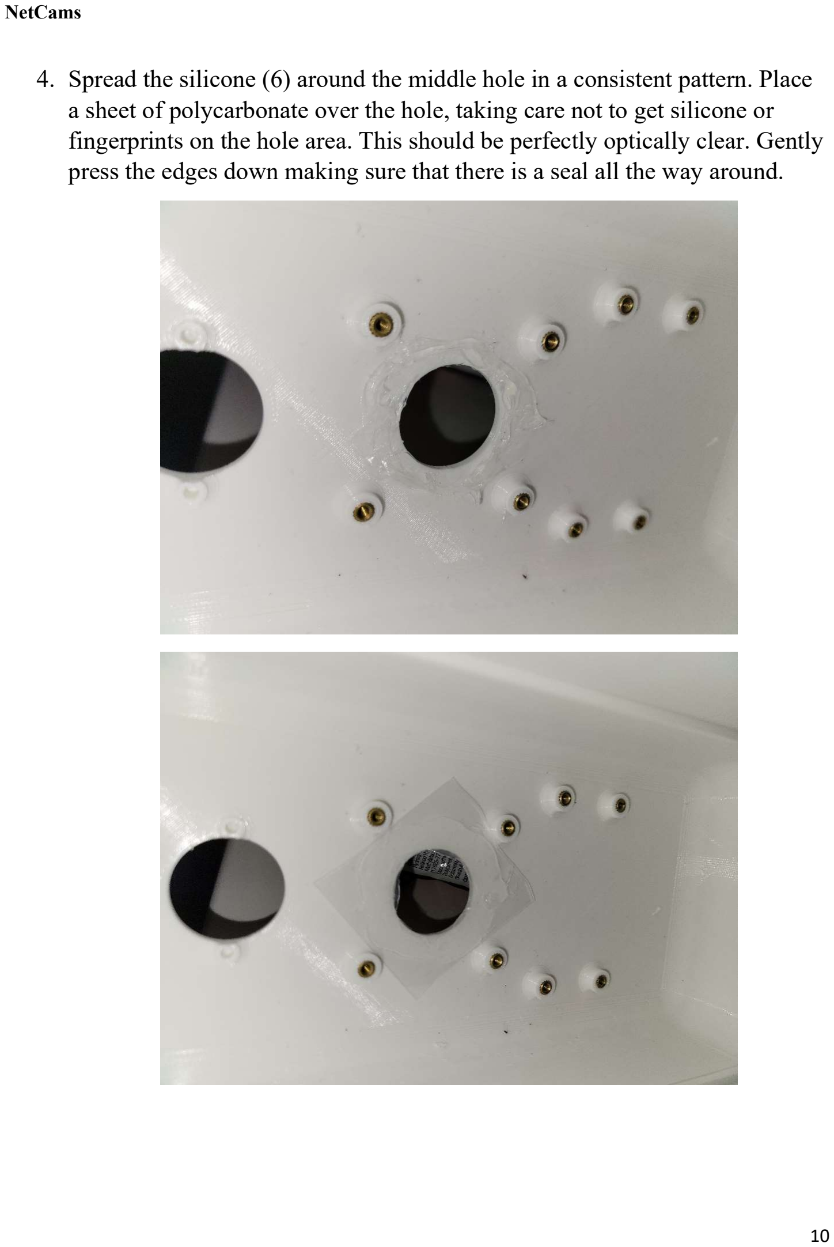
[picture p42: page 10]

10

### 4. Spread the silicone (6) around the middle hole in a consistent pattern. Place

a sheet of polycarbonate over the hole, taking care not to get silicone or fingerprints on the hole area. This should be perfectly optically clear. Gently press the edges down making sure that there is a seal all the way around.

11

### 5. Screw in the camera bracket using 4 X M2.5 screws (7). Apply silicone

sealant around the PIR sensor hole.

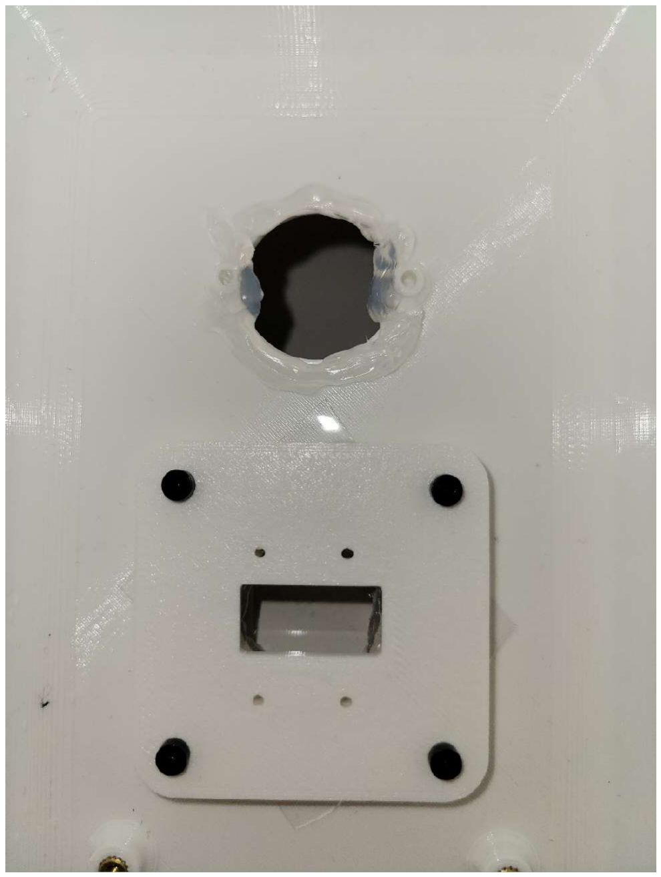
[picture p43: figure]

12

Note: It’s helpful to use a secondary RPi to check that the camera is focused correctly. Alternately, you could take a photo using the camera trap program and adjust the focus after. Additionally, before installing the RPi or the camera, they should be connected to each other. The RPi should also have its power cable installed.

### 6. Now, it’s time to install the electronics. First, use 2 X M2 screws (10) to

attach the PIR sensor (top). Use 4 X M2 screws (10) to attach the camera (middle). Use 4 X M2.5 screws (7) to install the RPi (bottom). Connect PIR sensor to RPi as shown.

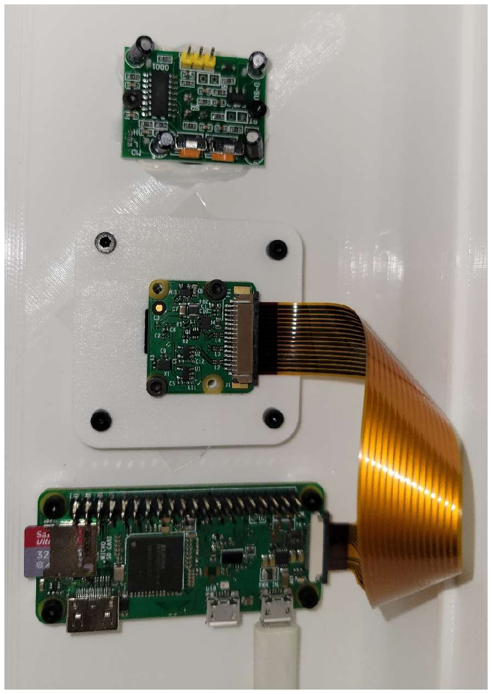
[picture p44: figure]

13

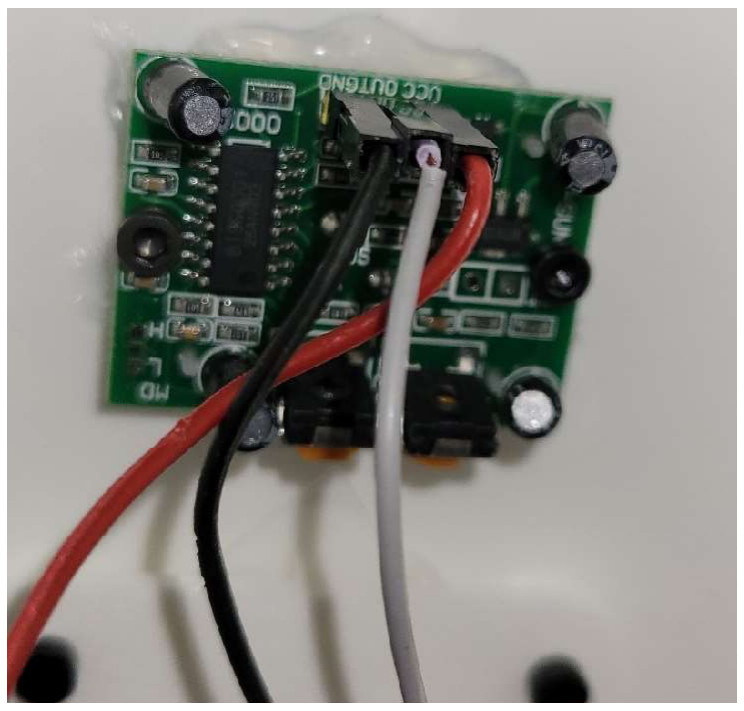
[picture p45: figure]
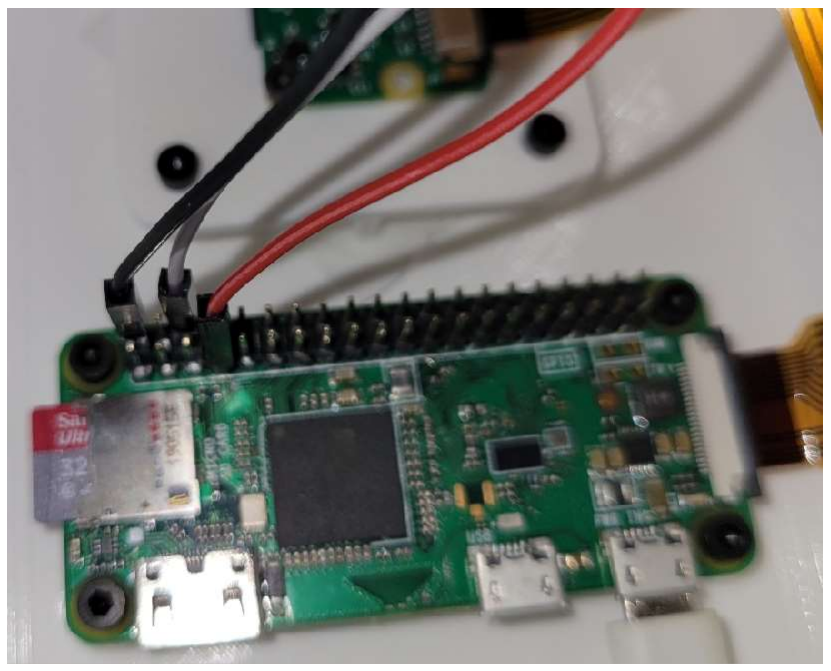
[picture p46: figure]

14

### 7. Lay the silicone tubing in the channel, taking care to start and end at the

bottom of the enclosure. Note the cut leaves an overlap between the start and end of the tube. This creates compression between the two ends and seals better.

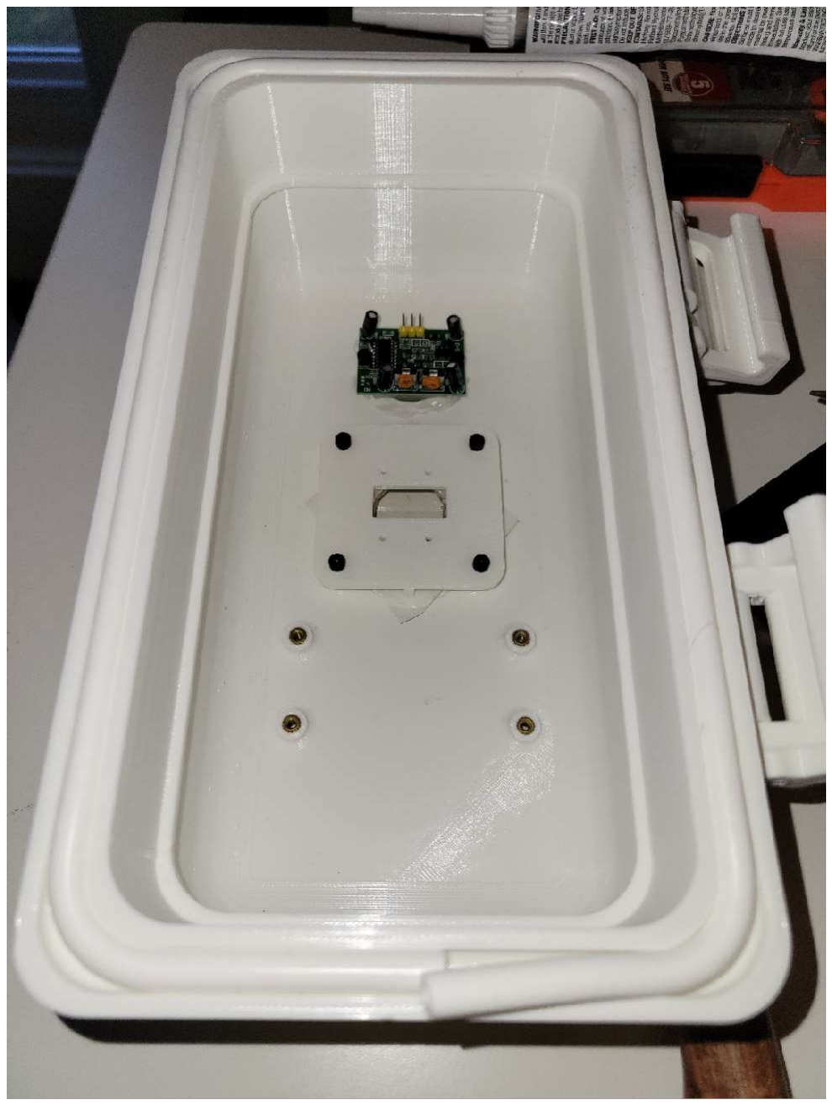
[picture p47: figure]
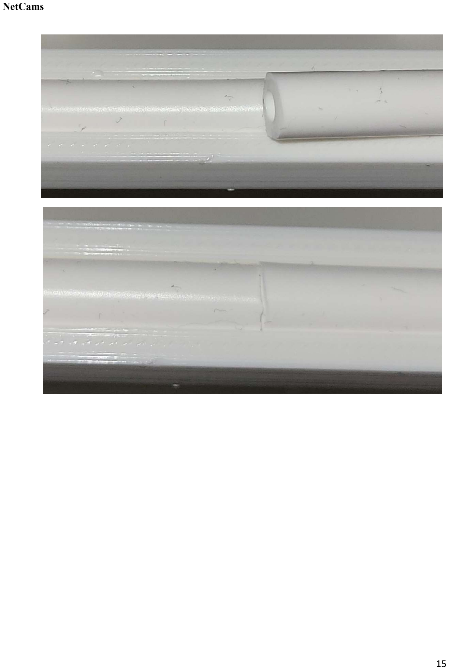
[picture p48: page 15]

15

16

### 8. Using 4 M4 washer (5), 2 M4 screws (3), and 2 M4 wing nuts (4) to install

the mounting hardware as shown.

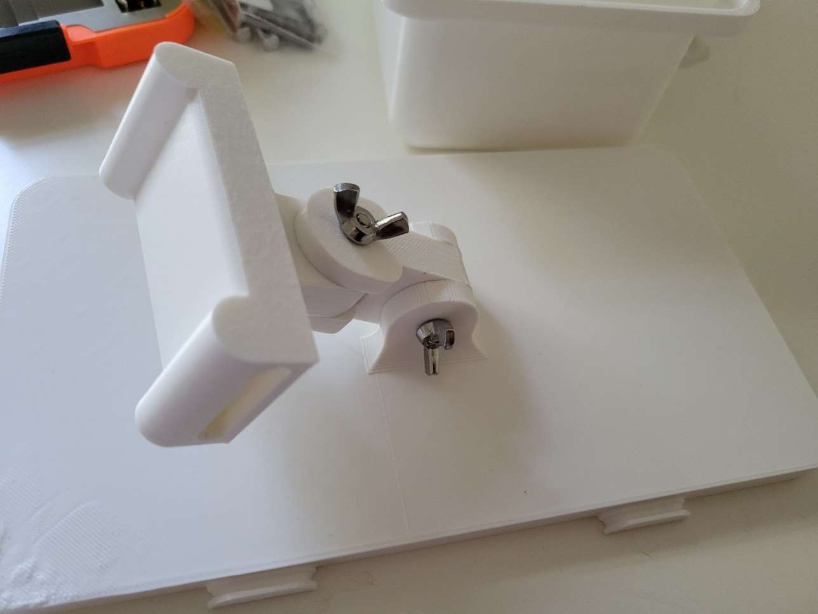
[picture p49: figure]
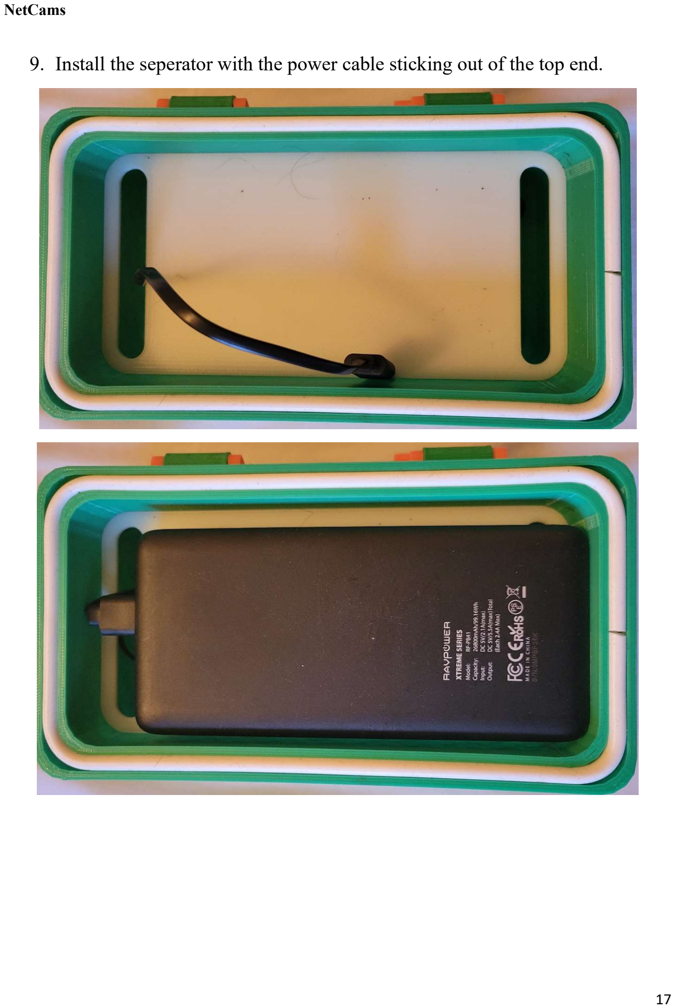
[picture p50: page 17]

17

9. Install the seperator with the power cable sticking out of the top end.

18

10 . Put the two parts of the enclosure together, and you’ve got yourself a NetCam!

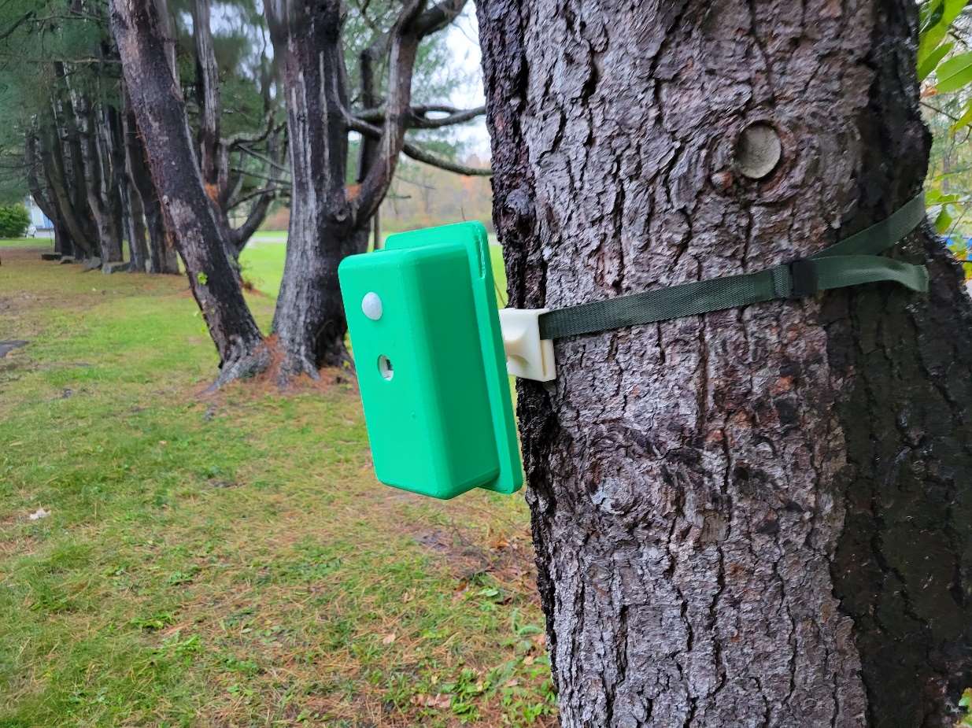
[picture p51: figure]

19


f

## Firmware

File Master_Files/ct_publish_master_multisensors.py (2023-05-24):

import paho.mqtt.publish as publish
from picamera import PiCamera
from time import sleep
import time
from gpiozero import MotionSensor
import socket
import datetime
import os
import shutil
import commands
from time import strftime
#Authors:
#Dylan Logan

#Master Publisher code for multiple sensors photo triggering
#Periodically polls the sensors in the camera array and takes a picture if a set ratio is met
setup = True 
main = False
take_pic = False
delay = False
initial_setup = True
delay_flag = 0
reinitialize = 0

while setup:
	if initial_setup == True: #runs only one time
		print("Started master multisensor photo sync program")
		photoNum = 1
		MQTT_SERVER = "localhost" #master Pi IP address
		MQTT_PATH = "test" #topic name for MQTT
		path = '/home/pi/cameraTrapPhotos/'
		pir = MotionSensor(4) #use motion sensor
		camera = PiCamera() #use camera
		access_rights = 0o777

		#create a directory if one does not exist for the camera trap photos
		if(os.path.isdir(path)==False):
			os.mkdir(path,access_rights)
		#else, remove all photos and photo sets currently in the directory
		else:
			for fname in os.listdir(path):
				shutil.rmtree(path+fname)

		IPAddr = commands.getoutput("hostname -I") #get Pi's own IP address
	
		#set socket for listening to slave pis
		s = socket.socket()
	
		s.bind(('',12345)) #bind the socket to a unused undesignated port
		initial_setup = False
		
	s.settimeout(30) #set a time for the socket to be open for. This is purposefully long in lue of a delay
	sensors_connected = [] #list of all the slaves that connect to the master
	message = "Setup"
	sensors_connected.append([str(IPAddr)])
	publish.single(MQTT_PATH,message,hostname=MQTT_SERVER) #send message see which slave sensors are looking to connect
	s.listen(4) #set socket to take a backlog of 10. increase number if there are more slaves to be connected
	print("Socket is listening for setup")
	
	while True:
		try:
			c,addr = s.accept() #accept connections from slave pis
			print('Got connection from', addr)
			receivedIP = str(c.recv(1024))
			sensors_connected.append([receivedIP])
			c.close()

		except socket.timeout:
			break
	
	total_sensors = len(sensors_connected)
	if (total_sensors > 3):
		thresh_pass = floor(2/3*total_sensors) #this creates the threshold to take a picture as two thirds of the total sensors rounding down
		main = True
	elif (total_sensors < 3): #if there is only one slave connected then the script is not run
		print("you dont have enough connected sensors")
	else: #this is the minimum number of sensors to create a usable model therefore it is a special case where all the sensors must detect heat
		thresh_pass = 3
		main = True
	setup = False #changes the setup variable to false so it only runs once
	wait_time = 10 #Want to get many pics of the animal when it comes so wait time is just long enough for sensors to cool down on average
	s.settimeout(10) #sets a new time for reading sensor outputs. shouldnt need to be this high
	break #ends the loop

#run continously until terminated by user
while main:
	print("Resting...")
	pass_flag = 0 #resets flags every loop
	sleep(wait_time)
	print("Starting")
	message = "Info"
	publish.single(MQTT_PATH,message,hostname=MQTT_SERVER) #send message get info about slave sensors

    #put sensor state of master pi in sensor list
	if(pir.motion_detected==True):
		pass_flag +=  1 #increments the pass count if motion is seen on master

    #listen for incoming connections
	s.listen(total_sensors) #now listens for exactly the correct number of sensors 
	print("Socket is listening")

    #get data from slave pis by listening to socket and parse it and add it to sensor list
	for i in range(1,total_sensors):
		try:
			c,addr = s.accept() #accept connections from slave pis
			print('Got connection from', addr)
			receivedInfo = str(c.recv(1024))
			
			if receivedInfo == "True":
				pass_flag += 1

			c.close()
			
			if pass_flag >= thresh_pass:
				take_pic = True

		except socket.timeout:
			total_sensors -=1 #this means a sensor has died
			reinitialize = 20950 #sets cameras so run for a short amount more time then reinitialize and rethreshold
			break #break the loop so no pic is taken as a timeout means the animal is likely past

	#list of all devices and their sensor readings  CAN ADD BACK IN FOR TESTING OR IF INTERESTED 
	#for x in sensorlist:
		#print(x)

    #if ratio is above the threshold, start a photo session
	if(take_pic):
		#Send MQTT message to slaves to take photo and start photo
		date = strftime("%d_%m_%y_")
		message = "Take Synced Photo " + str(photoNum) + ' ' + date
		
		publish.single(MQTT_PATH,message,hostname=MQTT_SERVER)
		ctpath = '/home/pi/cameraTrapPhotos/' + date +'set' + str(photoNum) + '/'
		access_rights = 0o777 #permissions for directory
        #make directory for current photo session
		try:
			os.mkdir(ctpath,access_rights)
		except OSError:
			print("creation of the directory %s failed" % ctpath)
		else:
			print("successfully created the directory %s" % ctpath)

        #set camera and file parameters
		filename = 'set'+str(photoNum)+'_camera1.jpg'
		camera.resolution=(3280,2464)

		#Take Photo
		camera.capture(ctpath+filename)
		#End of Photo session

		print("Camera 1 photo number "+ str(photoNum) + " taken")
		#go to next photo session
		photoNum = photoNum + 1
		
#		delay = True #tracks that a picture has been taken and that the delay should begin
		take_pic = False #stops the picture taking loop
		delay_flag +=1 
		sleep(6)


	if delay_flag == 10:
		delay = True
		delay_flag = 0
		
	reinitialize +=1 #increment every loop
	if reinitialize == 21000:  #about once a day will reinitialize the list of sensors 
		setup = True
		main = False
	while delay: 
		sleep(45) #Gives the sensors ample time to fully reset if they have just taken 10 pics in a row
			#Long times at high could cause them to continue to falsely read high for longer i.e. cool down
